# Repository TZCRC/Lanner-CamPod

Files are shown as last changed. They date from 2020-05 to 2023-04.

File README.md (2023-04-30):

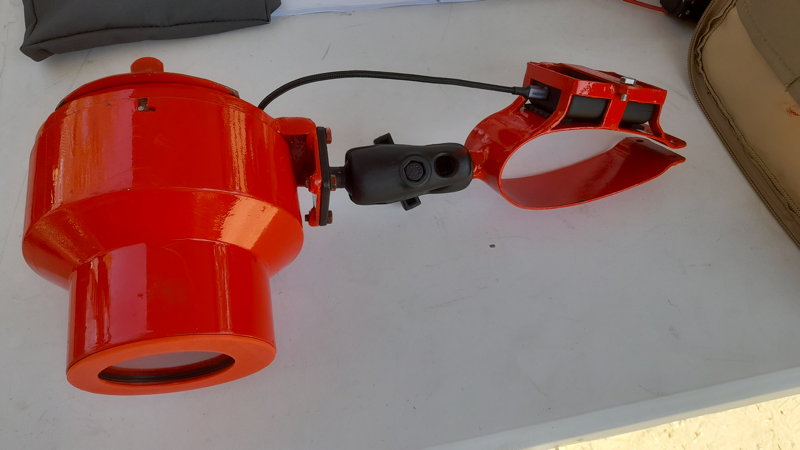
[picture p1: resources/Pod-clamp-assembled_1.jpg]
Lanner camera pod on Cessna


# Lanner CamPod

Oblique aerial photographs of wildlife and habitat are becoming an important part of aerial surveys. Some survey implementors have specially modified aircraft which allow cameras to be placed and operated  inside the aircraft cabin, but these modified aircraft are rare and it is extremely difficult and expensive to make modifications to standard aircraft. In 2018-2019 at the Tanzania Wildlife Research Institute we developed a relatively inexpensive oblique camera system that could be attached to any Cessna 172, 182 or 206 wing strut to get the same field of view as a human observer for a sample count. 

This document outlines the elements and usage of the v2 Lanner camera pod, and suggestions for further development. The v1 site is available as a [release](https://github.com/TZCRC/Lanner-CamPod/releases/tag/v1) (click then download and unzip).

Go to the code view to see all the resources

## Resources

* [_drawings](_drawings) - mechanical drawings for the pod housing.
* _hardware - 3D-printable components and equipment specifications
* _logger - files for setting up and configuring the OpenLog Artemis system.
## Attribution & Acknowledgements

Copyright Howard L. Frederick ([Tanzania Wildlife Research Institute](https://www.tawiri.or.tz)) 2018-2020.

Developed with support from [Vulcan Inc., Seattle, WA](https://www.vulcan.com/) and the Paul G Allen Foundation. 

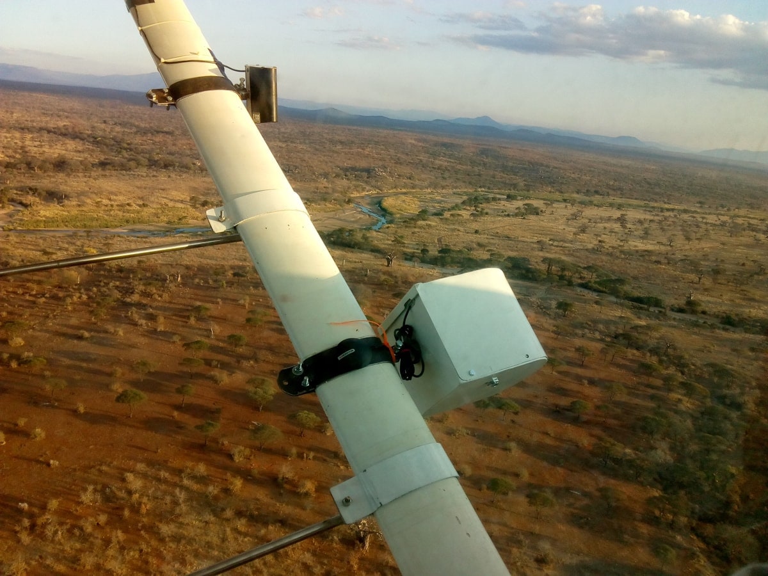
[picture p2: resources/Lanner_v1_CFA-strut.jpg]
The "Strut Digital Eyeball" in flight over Ruaha National Park, 2018.


## Aims & mission profile

The requirements of the camera system are to be able to take stable, hi-quality photographs on a continuous basis during flight, ideally with 50% overlap between images, and recording the angles of view to be able to reconstruct the geometry of the photographic footprint.

* Flight duration: 
  * Sample count flight with human observers: 3.5-4 hours;
  * Photographic-only flight: 4-7 hours.
* Metadata:
  * Camera image with time (subsecond) and general metadata (exposure, ISO, etc);
  * GPS XY and elevation (Z) synchronised via timestamp;
  * Heading, pitch, roll and yaw from IMU;

* Image capture
  * Images should be raw format (Nikon NEF), recorded at a minimum of 2 second intervals or faster;
  * Minimum storage capacity on board should be 1800 frames / hr * 4 hours * 35 MB / frame = 252GB.
  * Aperture set to maximum sharpness for the lens (F7.1 in the case of the f28mm lens);
  * Shutter speed at minimum 1/2000;
  * ISO set as auto-ISO to ensure shutter speed <= 1/2000. 

## Equipment

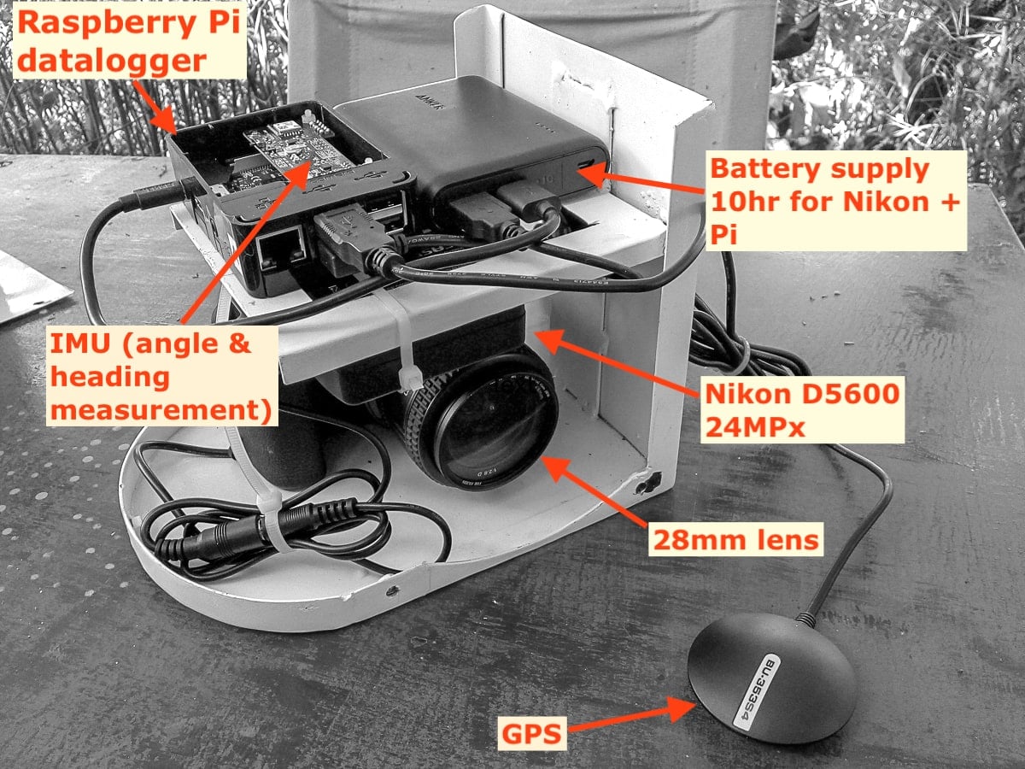
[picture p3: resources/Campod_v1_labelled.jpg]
Campod_v1_labelled


Each 'pod' consists of:

* DSLR or mirrorless ([EVIL](https://en.wikipedia.org/wiki/Mirrorless_camera)) camera.
* Power system:
    * For Sony a7-series, a PD powerbank with USB-C connection. See the [Power System](PowerSystem.md) page for important notes about these powerbanks and Sonys.
    * [Tethertools "Case Relay" battery](https://www.tethertools.com/product-category/power-management/case-relay-camera-power/) which acts as a sort of uninterruptible power supply, taking power from the battery bank and providing constant power to the camera, plus a USB battery bank with USB-A.
* Controller / logger: [a Sparkfun Openlog Artemis board](_logger/README.md):
    * Logs all data to a microSD card automatically.
    * GPS board attached by I2C (QWIIC) connector.
    * LiOn battery for ~ 10h of logging time.
* Cables:
    * USB-C power cable from external battery to camera.

* Housing: steel frame and skin, with screw mount through base for camera and large bolt connector to strut clamp. 

**Not yet implemented*

## Fieldwork so far and lessons learned

### 2022

Lanner pods were used extensively in Zambia during the 2022 KAZA aerial census. Field notes will be updated here soon.

### 2019:

A set of images was collected in Tarangire National Park with a redesigned housing system, where the camera pod was fitted to a microlight (Savannah) using a two-point attachment system.

For the RR-SL systems, a further 25,000 images were collected in the corridor between the two ecosystems as part of a trial monitoring system for the corridor (for WCS Tanzania).
### 2018:

Camera pods were trialled in Ruaha-Katavi-Lukwati (RR) and Selous-Mikumi (SL) ecosystems in late 2018 as part of the TAWIRI aerial survey programme. Surveys were primarily funded by WCS and FZS, respectively, and covered 90,000 km² and 110,000 km².

Approximately 200,000 images were collected in RR, and 150,000 in SL.

### Protocol

Ideal protocol follows

1. Anker battery bank was fully charged the evening before. Two bars (out of four) are enough for a whole 4-hour flight, though.
2. Time was set on the camera either manually (from GPS time) or with a USB connection on a laptop. 
3. Pods were attached to the aircraft ~ half an hour before flight. Cameras were set to mimic the field of view of the observer by visual inspection relative to the RSO camera position and the centre of the SRF rods.
   1. In test flights and later flights in SL the cameras were set at 45° angles.
   2. Clamps were left on the wing struts, and the pods slotted into the clamps each time (necessitating angle adjustment).
4. Before closing the housings, the cameras were set to trigger photos ~ 10 minutes after takeoff (enough time to reach closest transects) using the Interval Timer menu:
   1. Start time ~ 0715, but this depended on how close the transects were expected to start and how diligent the team was likely to be about getting into the air on time.
   2. Interval 2 seconds
   3. Number of photos 8000 (enough for 4.4 hours of data collection, which would exceed all but the longest possible collection time)
5. On return, cameras that were still running were manually turned off by reaching in through the porthole. Pods were disconnected from the clamp using the set screw (bolt) and disassembled in the workshop.
6. SD cards were removed from the cameras after flight and data were copied to an external harddrive and later to a backup.

### Performance

* Photographic quality was generally excellent, with easily-distinguishable wildlife down to impala size and smaller. 
* Images had noticable reduced sharpness at the edges at F5-F5.6 (which was the setting for most of the RR images). 
  * This criticism of sharpness is fairly personal, and the PI has been informed that he's being overly picky.
  * Tests determined better sharpness with aperture at F7.1, and later images were set accordingly. This results in better sharpness at the edges (particularly corners) of the image, but the image quality in these corners is noticably poorer.
  * A better lens is needed - turns out this one (Nikkor 28mm) is not known as being terribly sharp. However, it's unsure if a decent combination of small size, focal length and good sharpness is possible. The Sigma Art 28mm is incredibly good but  larger in length, overall volume and weight.
* Auto-ISO settings with 1/2000 speed and any allowable ISO up to 25,600 meant motion blur was unnoticable. The higher ISO values - particularly in the early morning, had a lot of noise, but by the time the target area was 
* The combination of fast shutter speed and the rubber mounts on the connector from housing to clamp seem to have reduced any significant vibration as well, compared to the results that Richard Lamprey reports from a fixed (steel-on-steel) mount from Tsavo.
* The Anker battery in line with the TT for the Nikon is enough to power > 10K shots on the D5600. However, several times the pod returned with the the Anker still full and the TT empty, having captured ~ 3K images before the TT was low. Apparently the TT gets a full charge then stops drawing power, at which point the Anker turns itself off and the TT runs down. 
  * *This is prevented by having the RPi attached at the same time, which ensures enough current draw to keep the Anker on line.*
* Time stamps for the IMU data were not correct until a software update was made for the Selous work. The RPi is supposed to set its internal clock from the GPS signal but this was not working (in Ruaha-Msembe we had wifi which the Pi units were connecting to and getting time info, and this obscured the fact that the NMEA signal wasn't working for the `ntp` function). **Angle information is not necessarily correct for any of the first sets of images collected.**
* GPS data were logged to NMEA files, and the USB GPS units seemed to function within a minute or two of boot.
* Copying image data from the SD cards to hard drives was tedious and something of a limiting factor. With 7-8,000 images collected per flight, typically 150GB of data needed to be copied, and this took > 1 hour per SD card. 

## Optimisations / development

* Time management for the RPi and camera are vital, and there are shortcomings and uncertainties:
  * How can the NMEA (GPS) time setting be made more reliable? How poorly does it actually work?
  * How much drift is there in the clock during survey flights?
  * How accurate is a timestamp logged to a file when it comes from the GPS? Or recording a 'trigger' action on the camera? Is there a large latency in the USB or GPIO system?
  * **How does the timestamp of IMU data relate to the timestamp of the GPS log?**
* RPi should probably log NMEA and IMU data to a single database (SQLite?) - unless just logging to a text file is more robust?
* Communication between the camera and RPi are needed:
  * GPIO trigger of shutter instead of relying on the timing system;
  * Log data collected from USB at some frequency - battery level / storage status in particular.
* Communication with an Android phone is needed, giving:
  * Status of storage on phone, battery level, state of photo capture.
  * Control of triggering and interval options.

## ToDo list

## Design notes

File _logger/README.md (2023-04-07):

# OpenLog Artemis settings

The [Sparkfun OpenLog Artemis](https://www.sparkfun.com/products/19426) is a small board with integrated IMU[^1] and microSD card slot, which immediately starts logging data to the SD card when power is connected. It can be attached to a wide variety of sensors, including the GPS unit used here. 

Settings for logging camera pod IMU and GPS data using the Openlog Artemis (OLA) and the ublox ZOE-M8Q GPS unit with QWIIC connection.

To use, copy the two *.txt files to the SD card being used by the OLA, overwriting anything that was there before.

Settings:

* 10Hz logging speed.
* YYYYMMDD date-time format.
* GPS: log heading, ground speed.
* IMU QUAT6 quaternion values recorded.
* Log microseconds
* Log DMP compass

[^1]: As of late 2022 and early 2023, the version of the Artemis sold is **without the IMU** chip due to supply chain issues. However, there are QWIIC IMU board options available.

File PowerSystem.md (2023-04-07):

# Power supply for camera pod

Power is needed to run the camera and the RPi for a 5+ hour mission.

## Power requirements

### Sony Alpha 7s

Unlike many other cameras, the Sony a7 series can be powered by a USB powerbank and cable.

* The powerbank must be a "power delivery" (PD) model, capable of delivering at least 18W of power. Other powerbanks may seem work, but the internal battery and the external will be drained simultaneously and **the camera body can get very hot**. Testing is vital.
* Test the USB cable from power bank to camera - not all cables are made equal (by a long shot), and you may find that a good _data_ cable doesn't provide enough wattage to run the camera. In contrast, the uGreen cables used for fieldwork were poor for data but had excellent power capacity.

### Nikon

Normal EN-EL5a battery:
* nominally 7.4V 1kmAh -> 7.5Wh battery.
* Lasts for ~2,700 images

External power supplies:
* AC-DC easy to find on Amazon but require a 120 or 240VAC source.
* DC from USB powerbank and via the Tethertools connector and dummy battery.

## Power tests

2022 Bench testing

* Sony a74
* Powerology 10Ah powerbank
* 2s intervals.

~ 9h of operation until SD card filled up.

2018-09-10 Bench test with full system
* Anker power supply ~ full
* CRelay on red (low power)
* D5600 JPG
* RPi running GPS script

Got 5 hours of actual operation; both GPS log and photos end at same time.

## Field tests

Units were powered with the Tethertools external battery connected to the Anker power supply by USB. 
* Power was enough for 5hr missions, using less than half the power indicated on the Anker.
* **Power failed** when the RPi was not also attached to the Anker and running. The unit would return having drained the Tethertools battery and the Anker still fully charged - apparently when the TetherTools unit stops drawing a certain current (i.e. when full or close to it?), the Anker would turn itself off and not resume. When the RPi was attached and drawing power, the Anker stayed on and powered both Pi and TT.

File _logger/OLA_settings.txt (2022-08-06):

sizeOfSettings=168
olaIdentifier=291
nextSerialLogNumber=1
nextDataLogNumber=30
usBetweenReadings=100000
logMaxRate=0
enableRTC=1
enableIMU=1
enableTerminalOutput=1
logDate=1
logTime=1
logData=1
logSerial=1
logIMUAccel=1
logIMUGyro=1
logIMUMag=1
logIMUTemp=1
logRTC=1
logHertz=1
correctForDST=0
dateStyle=2
hour24Style=1
serialTerminalBaudRate=115200
serialLogBaudRate=9600
showHelperText=1
logA11=0
logA12=0
logA13=0
logA32=0
logAnalogVoltages=1
localUTCOffset=0.00
printDebugMessages=0
powerDownQwiicBusBetweenReads=0
qwiicBusMaxSpeed=100000
qwiicBusPowerUpDelayMs=250
printMeasurementCount=0
enablePwrLedDuringSleep=0
logVIN=0
openNewLogFilesAfter=0
vinCorrectionFactor=1.47
useGPIO32ForStopLogging=1
qwiicBusPullUps=1
outputSerial=0
zmodemStartDelay=20
enableLowBatteryDetection=0
lowBatteryThreshold=3.40
frequentFileAccessTimestamps=0
useGPIO11ForTrigger=0
fallingEdgeTrigger=1
imuAccDLPF=0
imuGyroDLPF=0
imuAccFSS=0
imuAccDLPFBW=7
imuGyroFSS=0
imuGyroDLPFBW=7
logMicroseconds=1
useTxRxPinsForTerminal=0
timestampSerial=0
timeStampToken=10
useGPIO11ForFastSlowLogging=0
slowLoggingWhenPin11Is=0
useRTCForFastSlowLogging=0
slowLoggingIntervalSeconds=300
slowLoggingStartMOD=1260
slowLoggingStopMOD=420
resetOnZeroDeviceCount=0
imuUseDMP=1
imuLogDMPQuat6=1
imuLogDMPQuat9=0
imuLogDMPAccel=0
imuLogDMPGyro=1
imuLogDMPCpass=1
minimumAwakeTimeMillis=0
identifyBioSensorHubs=0
serialTxRxDuringSleep=0
printGNSSDebugMessages=0

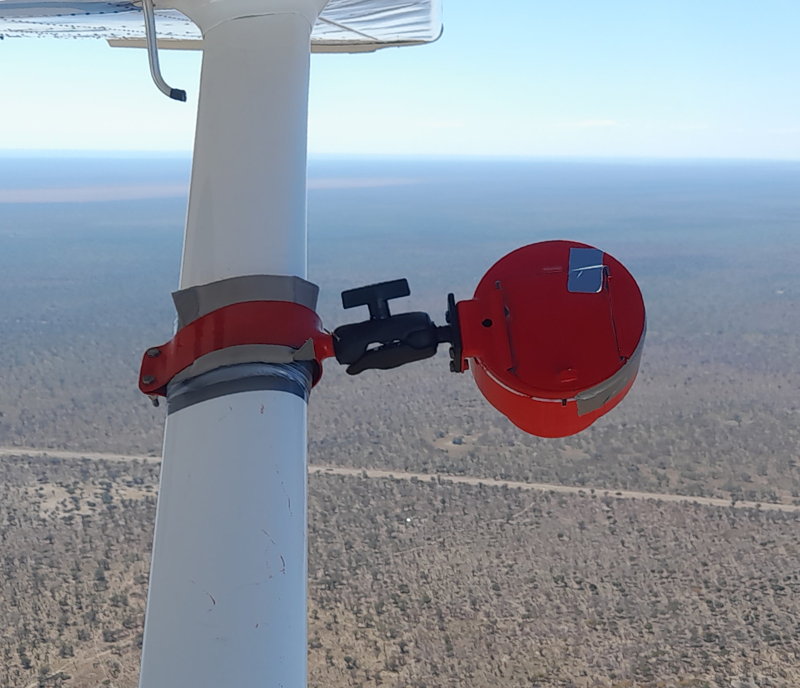
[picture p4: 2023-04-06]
resources/Lanner_v2_aerial_1.jpg

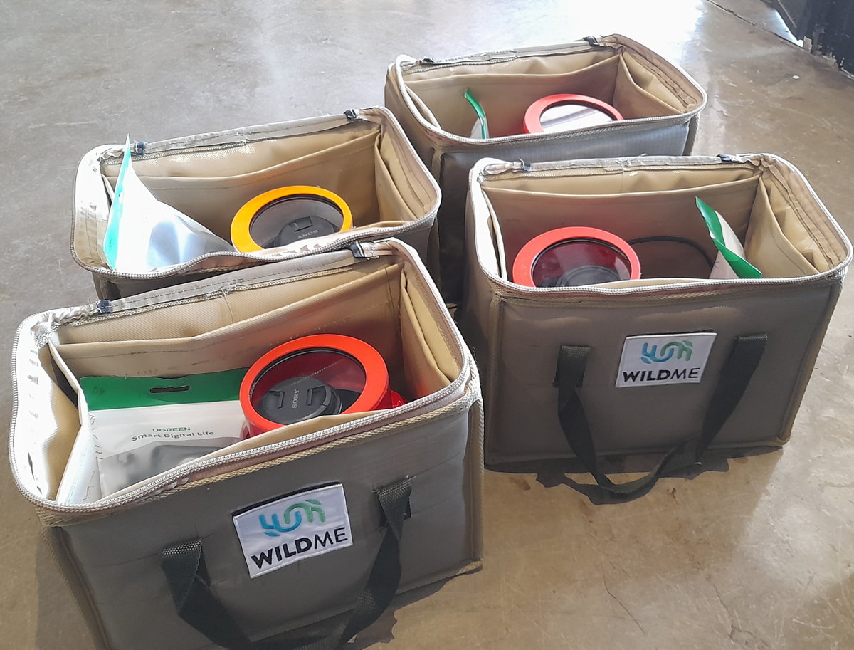
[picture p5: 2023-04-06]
resources/LannerPodBags-x4.jpg

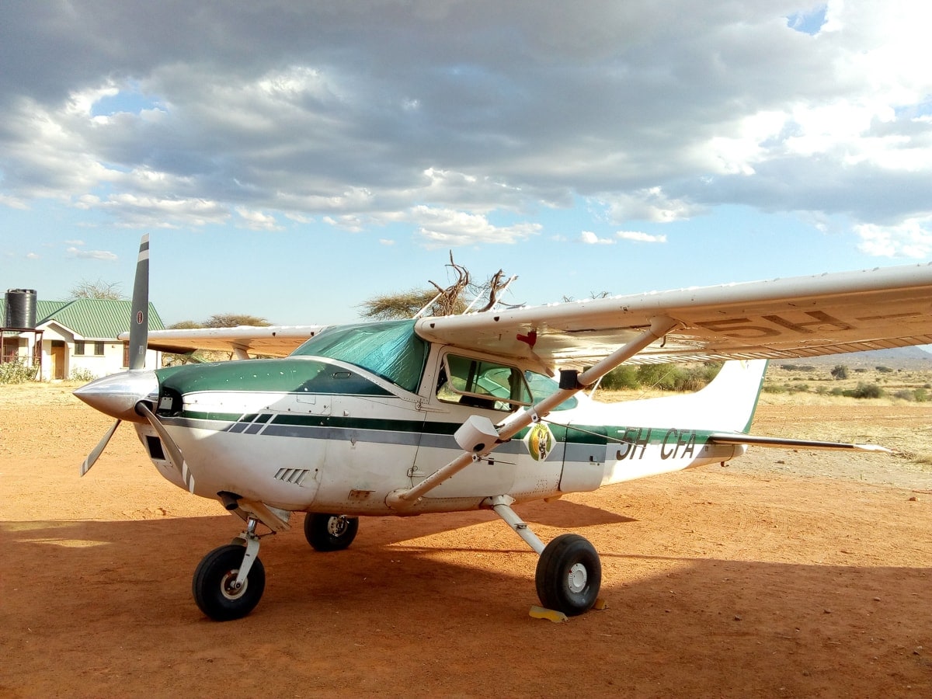
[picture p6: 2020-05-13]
resources/Lanner_v1_CFA.jpg

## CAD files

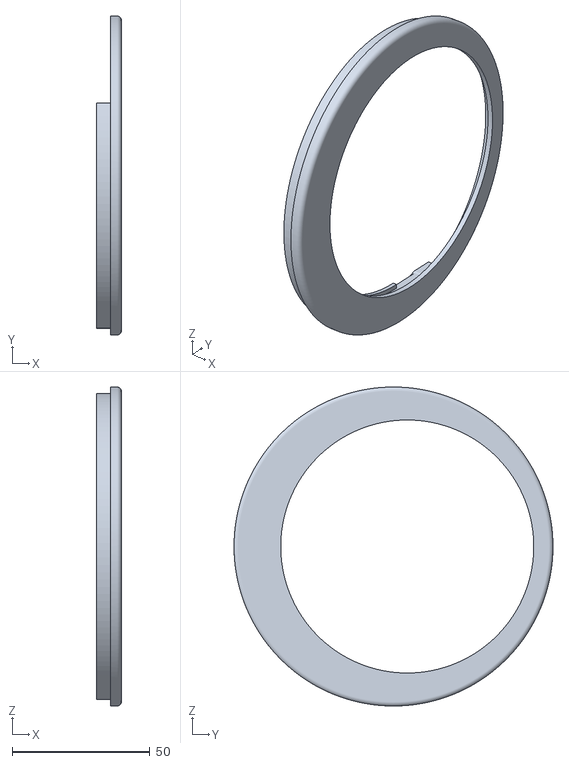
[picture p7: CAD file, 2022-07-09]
_hardware/3D_print/PVC_cap.stl
9.00 x 116.0 x 116.0

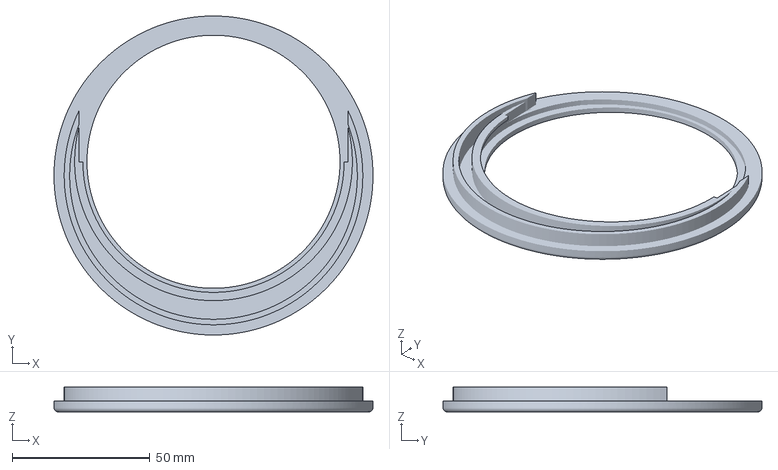
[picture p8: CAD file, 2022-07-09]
_hardware/3D_print/PVC64-cap-filter.3mf
116.0 x 116.0 x 9.00 mm

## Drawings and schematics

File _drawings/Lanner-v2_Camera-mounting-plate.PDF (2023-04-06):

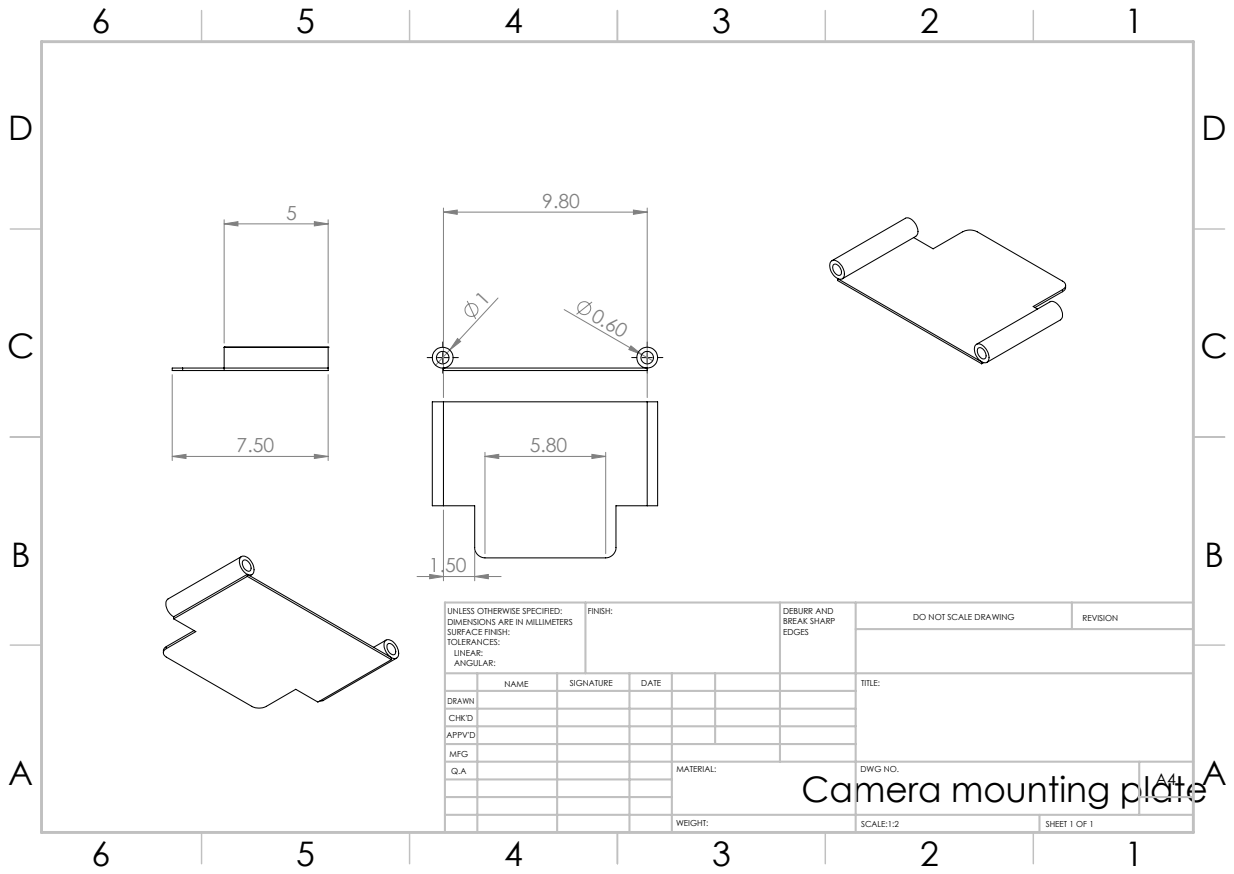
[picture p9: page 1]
FINISH:; DEBURR AND; BREAK SHARP; DO NOT SCALE DRAWING; REVISION; SCALE:1:2; SHEET 1 OF 1

UNLESS OTHERWISE SPECIFIED:
DIMENSIONS ARE IN MILLIMETERS
SURFACE FINISH:
TOLERANCES:
LINEAR:
ANGULAR:

NAME | SIGNATURE | DATE | | | | TITLE:

DRAWN
CHK'D
APPV'D
MFG
Q.A | | | | MATERIAL: | DWG NO. | A4

Camera mounting plate

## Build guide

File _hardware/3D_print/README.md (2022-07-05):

# 3D printable parts

* PVC_cap - an optional cover for the PVC housing, with space for a 95mm filter. Doesn't make it 
waterproof but certainly protects from some moisture and dust.

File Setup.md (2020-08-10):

# Setting up and using the camera pod and electronics

This is a brief overview to constructing and setting up a Lanner camera pod system for use in light aircraft. 

* The main software setup for the Raspberry Pi is [here](_rpi/PiNotes.md).
* Hardware availability has changed in the past 36 months and will be updated soon, but see the diagram in [the main README](./README.md) for the major components.

Also see:

* [Power system notes](./PowerSystem.md)
* [Overview README](./README.md)

## Attribution & Acknowledgements

Copyright Howard L. Frederick ([Tanzania Wildlife Research Institute](https://www.tawiri.or.tz)) 2018-2020.

Developed with support from [Vulcan Inc., Seattle, WA](https://www.vulcan.com/). 

Shield: [][cc-by-sa]

## Documentation license

This work is licensed under a
[Creative Commons Attribution-ShareAlike 4.0 International License][cc-by-sa].

[][cc-by-sa]

[cc-by-sa]: http://creativecommons.org/licenses/by-sa/4.0/
[cc-by-sa-image]: https://licensebuttons.net/l/by-sa/4.0/88x31.png
[cc-by-sa-shield]: https://img.shields.io/badge/License-CC%20BY--SA%204.0-lightgrey.svg

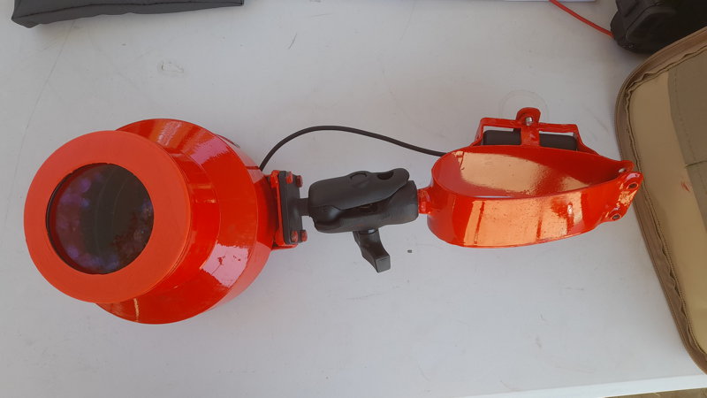
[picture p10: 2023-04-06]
resources/Pod-clamp-assembled_2.jpg

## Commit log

2018-08-15 New oblique code and power system notes.
2018-11-03 Added calibration script
2019-01-22 Update on power system experience from the field.
2019-01-25 Updated notes and background info on obliques
    [camera_data.csv]
2022-07-05 Added 3D printing folder
    [PVC_cap.stl]
2022-07-05 3D printing readme.
2022-07-09 Cap filter v1
    [PVC64-cap-filter.3mf]
2022-07-09 PVC cap with +3mm fit
    [PVC_cap.stl]
2023-04-06 Updated power and camera specs
2023-04-07 Artemis and power system docs

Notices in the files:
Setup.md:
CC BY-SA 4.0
